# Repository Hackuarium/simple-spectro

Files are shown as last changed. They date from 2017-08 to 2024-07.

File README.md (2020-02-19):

# DIY spectrophotometer

## How to use it ?

Please check the [userguide](docs/5-use) to obtain all the useful information about the user interface.

## Goal of the project

This project was done at the [Hackuarium](http://www.hackuarium.ch/en/) association, a DIY biology hacking-space and open laboratory located in Ecublens (Switzerland). Feel free to [contact us](https://form.jotformeu.com/71600609780354) if you would like additional information or would like to buy a fully built and tested spectrophotometer.

Recently, the open-source and open-hardware community has been involved in the creation of open scientific tools. In this context, a few spectrophotometer projects emerged. However, none of them was sufficiently evolved to be casually used in a laboratory. It is for this reason that we started this project.
Our goal was to create a simple spectrophotometer that measures the
absorbance of a sample for 3 different light colors (red, green, blue), that is
self-contained (battery powered) and displays the result on a LCD screen. In addition, the tool had to be reliable, precise and cheap.

The initial idea was that you could teach spectrophotometry without
having to buy an expensive instrument, since you can find experiments
that do not require a specific light wavelength. This includes
optical density for bacteria culture, determination of a pigment's concentration in
a solution, determination of the kinetic of a reaction and many others.

The device is rather cheap, for you can buy all the components on AliExpress
(but one) and either 3D print or laser cut the case (MDF or acrylic glass). When constructing 10, the price
per spectrophotometer is around $30. However if you want to have a final
product with an aluminium case and PCBs already assembled, the cost would rather be $90 each if you order 20 of them.

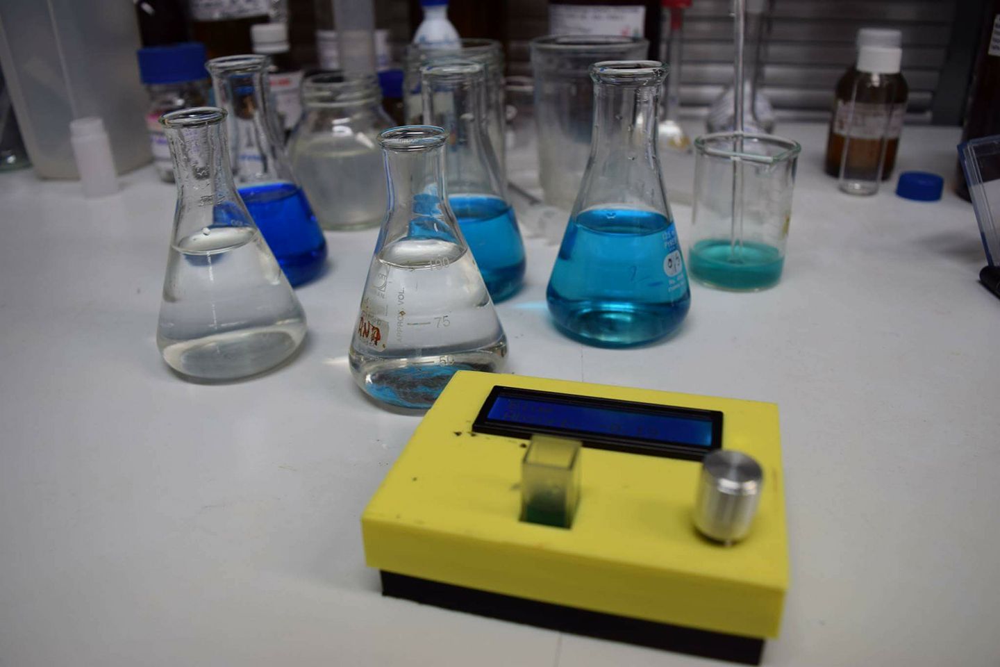
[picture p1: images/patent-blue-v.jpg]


## Can we do science with this ?

Before trying to explain how it is done more in detail maybe the first
question that we should answer is : can we do science with this tool?
When thinking about the design of the spectro, we found an light sensor that converts the light energy to frequency and that is linear on a range of nearly 10^6. This means that the luminosity range that we can measure precisely is really big. Only the precision of the component is therefore really promising and shows that we could do something that gives good results.

And indeed, the final product gives really accurate results in fields like:

- [Chemistry](docs/6-applications/chemistry/README.md)
- [Biology](docs/6-applications/biology/README.md)

And other, which you can see on [our lab notebook](experiments/README.md).

## Some of our results

### Patent blue V

To begin we did a very simple experiment that allows to measure the absorbance of solutions containing different known concentrations of patent blue V (E131), a blue pigment that is used in various blue candies.

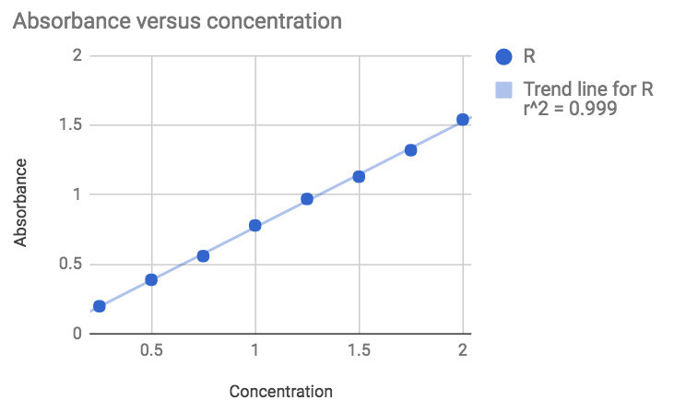
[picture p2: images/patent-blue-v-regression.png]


The result is rather good knowing that the solutions were simply prepared by adding various volumes (0 to 2 mL) of a concentrated pigmented solution with a 1mL seringe to 100mL of water. Not the most accurate method...

### Escherichia coli

Another feature of the simple-spectrophotometer is that it works on a rechargeable battery (autonomy of 48 hours). Consequently, you can measure a kinetic by placing the device directly inside an incubator, which is not feasible with a regular commercial spectrophotometer.

Optical density (OD) at 600nm is often used in biology to determine the biomass increase versus time. In this experiment we have placed Escherichia coli with cell growing media directly in the spectrophotometer cuvette and placed the spectrophotometer itself on a shaker in the incubator.
We can then program it to measure the absorbance every X seconds. In our case we measured the absorbance every 30 minutes (up to 40 measures). The following curve was obtained.

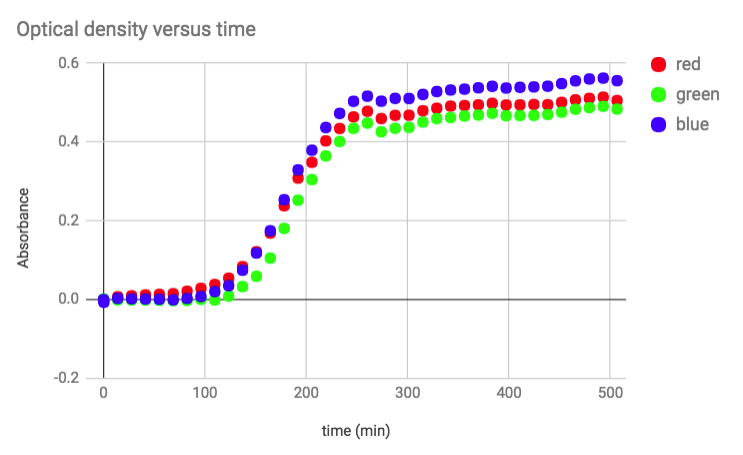
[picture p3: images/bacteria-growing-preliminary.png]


This experiment clearly shows the log phase and the stationary phase. But the growth was faster than expected. An acquisition every 15 minutes would have been a better choice.

## Using the simple spectrophotometer to teach science

The use of the spectrophotometer is rather simple. Just put a blank, press the button, wait 10s and put the sample. The result is displayed on the screen. In addition, it could be open so that students could see how it is inside and could really understand how the tool works (avoiding the "black box" effect). Also, since it is inexpensive, having ten of these for a classroom would be possible, which would allow students to have one instrument per pair.

[Using the spectrophotometer](https://www.youtube.com/watch?v=ZfckWQn0Nws)

For all this reason, we also consider our instrument as a pedagogical tool. This allowed us to use it to teach some basic scientific concepts to groups of children and teenagers.

[School in Mondomo (Colombia)](https://www.youtube.com/watch?v=Be6p4-nW06k)

## How to make it ?

The electronic design is compatible with the Arduino platform. We use an
ATMEGA32U4 microcontroller which is directly connected to the peripherals we need for this spectrophotometer.

We prefer to design the full PCB rather than to make a shield for an existing Arduino board. Indeed, the extra work to add the microcontroller is rather limited, so it does not make sense from our point of view to create a shield. Also, the resulting board is smaller and more reliable.

All the components we use but one are mainstream and can be found on eBay or AliExpress. The only special component is the light to frequency converter [TSL235R](https://www.sparkfun.com/datasheets/Sensors/Imaging/TSL235R-LF.pdf)
that we buy on [Mouser website](http://www.mouser.com).

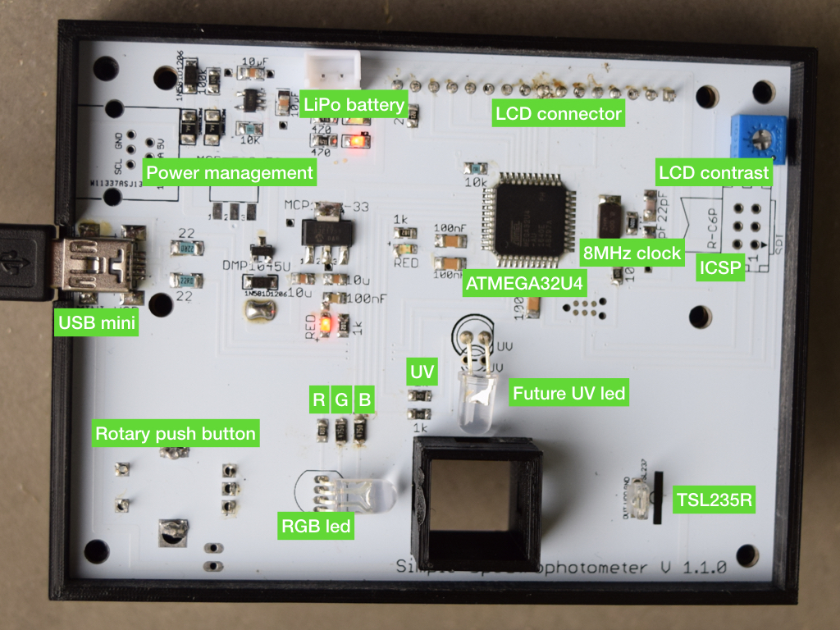
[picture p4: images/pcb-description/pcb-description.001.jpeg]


For more details about the construction process, follow one of the links underneath.

- [The PCB](docs/1-pcb) (using eagle)
- [The case](docs/2-case) (using FreeCAD and OpenSCAD)
- [The software](docs/3-software) (using Arduino)

## Experiments

- [Bacteria growth](experiments/bacteria/README.md)
- [Pigment concentration](experiments/color/README.md)
- [Measure of the fluorescence](experiments/fluorescence/README.md)
- [Kinetic of a reaction](experiments/kinetic/README.md)

## Tests

Underneath, you will find some of the tests we have run to verify the quality of our spectrophotometer.

- [Battery](docs/4-tests/battery)
- [Reproducibility of results](docs/4-tests/stability)

# Workshop

We regularly organize one day workshops "Build your own spectrophotometer" during which the participants learn all the process we went through to obtain the final product and build their own spectrophotometer. Please [contact us](https://form.jotformeu.com/71600609780354) if you are interested by this kind of workshop.

Here are the slides of the presentation we make during the workshop.

- [Slides](docs/7-misc/workshop/slides.pdf)

## Cloning the project

This project uses SUBMODULES.

In order to clone it use:

`git clone --recurse-submodules https://github.com/hackuarium/simple-spectro`

To update the submodules:

`git submodule update --recursive --remote`

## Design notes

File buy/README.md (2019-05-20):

## Buy the spectrophotometer

## DIY versions

The DIY versions are spectrophotometers to assemble yourself. You receive a preprogrammed PCB (all the SMD components are already soldered) as well as all the through holes components and parts to build a case.

### Eco-spectro

You receive all the required parts to construct a spectrophotometer and a case in MDF.

**Price:** 60 CHF + shipping (10 CHF)

### Bio-spectro

You receive all the required parts to construct a spectrophotometer and a case in black plexiglass.

**Price:** 70 CHF + shipping (10 CHF)

### Chimio-spectro

You will receive a case in black plexiglass with a transparent background so that you can easily understand how it works and explain it to others.

You will also get 50mg of E131 that allows to determine the concentration of pigments present in candies.

**Price:** 70 CHF + shipping (10 CHF)

### How to buy it

You can directly buy it online and receive it via mail at your place.

Please note that if you want to power it with a battery you have to buy one yourself.

<form action="https://www.paypal.com/cgi-bin/webscr" method="post" target="_top">
<input type="hidden" name="cmd" value="_s-xclick">
<input type="hidden" name="hosted_button_id" value="76TH95GMW5DSS">
<table>
<tr><td><input type="hidden" name="on0" value="Select the DIY model">Select the DIY model</td></tr><tr><td><select name="os0">
	<option value="Eco spectro">Eco spectro 60.00 CHF</option>
	<option value="Bio spectro">Bio spectro 70.00 CHF</option>
	<option value="Chimio spectro">Chimio spectro 70.00 CHF</option>
</select> </td></tr>
</table>
<input type="hidden" name="currency_code" value="CHF">
<input type="image" src="https://www.paypalobjects.com/en_US/CH/i/btn/btn_buynowCC_LG.gif" border="0" name="submit" alt="PayPal - The safer, easier way to pay online!">

</form>

## Pro version

The pro spectro comes fully assembled, tested and in an aluminium milled anodised case.

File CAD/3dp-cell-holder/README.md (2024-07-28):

# Goal
This 3D printed part allows the replacement of the four small parts holding the test sample cell while letting light pass through small orifices.

# Advantages of this design
- Fewer parts make the assembly easier.
- The cell is better held, preventing variation in results due to changes in the orientation of the cell.
- A side extension wall prevents the UV LED from directly lighting the sensor.
- A bottom wall prevents light from coming through gaps at the bottom of the cell, ensuring more consistency in test conditions.

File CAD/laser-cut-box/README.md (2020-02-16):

## Using lightburn

Preferences may change depending the cutting machine. In our case:

- add an offset of 0.07 on all inside parts (assemble)
- power 100% speed 18%

## It's in the box

#### An OpenSCAD project to wrap your PCB in a box

Often we need to create custom boxes to wrap a printed circuit board (PCB) and this
may be time consuming.

In this project based on couple of parameters you can quickly and efficiently create DXF files that after laser cutting will provide the different elements to create the box. You may cut any number of holes (round or rectangle) on all the faces of the box and the coordinates will always be relative to the (0,0) that is the bottom left of the PCB.

Coordinates [x,y] of holes corresponds to the center.

You can render the box as a 3D image



And you can also export easily as a SVG of DXF file for laser cutting.



## How to use it

Download OpenSCAD and open the file 'testBox.scad'.

The comments in the file should be clear enough to use this code.

## Exporting as DXF

You should change the following parameters before generating DXF:

- showLabels = false
- 3d = false

You may then render the image and export as DXF.

## Code example

```js
$fn=40;

use <pcbbox/pcb.scad>;

pcb(
    length=100,         // length of the PCB
    width=80,           // width of the PCB
    padding=1,          // space around the pcb (between pcb and box)
    thickness=3,        // thickness of the material to create the box
    pcbThickness=1.6,   // thickness of the box
    topToTop=20,        // distance from the top of the PCB to the external top of the box
    bottomToBottom=40,  // distance from the bottom of the PCB to the external bottom of the box
    extend=10,          // should top and bottom 'extend' in order to assemble the box without glue
    screws=[            // position of holes to fix the PCB
        [5,5],
        [10,70],
        [85,15],
        [80,60]
    ],
    screwDiameter=3,    // diameter of the screws to fix the PCB
    topHoles=[          // holes to put on the top of the box
        [20,20,30,10]   // 0,0 is the bottom left of the PCB
    ],
    bottomHoles=[       // holes to put on the bottom of the box
        [40,40,10],     // array witlh 3 parameters = a circle [x,y,diameter]
        [20,20,5,5]     // array with 4 parameters = a rectangle [x,y,width,depth]
    ],
    frontHoles=[        // holes in front of the box, over the PCB
        [20, 2.5, 5],
        [40,5,10,10]
    ],
    frontHolesB=[       // holes in front of the box, under the PCB
        [20,2.5,5],
        [40,5,10,10]
    ],
    backHoles=[         // holes in the back of the box, over the PCB
        [20,2.5,5],
        [40,5,10,10]
    ],
    backHolesB=[        // holes in front of the box, under the PCB
        [20,2.5,5],
        [40,5,10,10]
    ],
    leftHoles=[         // holes on the left of the box, over the PCB
        [20,2.5,5],
        [40,5,10,10]
    ],
    leftHolesB=[        // holes on the left of the box, under the PCB
        [20,2.5,5],
        [40,5,10,10]
    ],
    rightHoles=[        // holes on the right of the box, over the PCB
        [20,2.5,5],
        [40,5,10,10]
    ],
    rightHolesB=[       // holes on the right of the box, under the PCB
        [20,2.5,5],
        [40,5,10,10]
    ],
    showLabels=true,    //should we show the labels
    labelsSize=10,      // size of the labels
    3d=true             // 3d rendering or just 2d ?
);
```

## Screwing the PCB

We recently often use black nylon M3 screw, standoff and spacer.

In order to fix the PCB we have the following sequence:

- M3 screw
- top of the case
- column standoff female spacer
- PCB
- column standoff male spacer
- bottom of the case
- M3 screw (we take 40 mm screws that we cut if needed)



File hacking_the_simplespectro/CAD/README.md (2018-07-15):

This folder contains the files of the final version of the spectro-plongeur. The svg files can be opened in easel.inventables.com (a free account can be created) to change the cut settings and start the CNC (an X-Carve 1000mm x 1000mm).

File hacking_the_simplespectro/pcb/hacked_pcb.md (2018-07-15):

# What has been modified on the PCB ?

- 2 blue LEDs instead of 1 UV and 1 RGB (2 pins are not used)
- 22 Ohm blue LED resistance instead of 1000 Ohm so that both LEDs have equal power
- cables (26W) to connect the PCB to the spectro-plongeur

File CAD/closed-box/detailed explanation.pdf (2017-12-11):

## Spectrophotometer

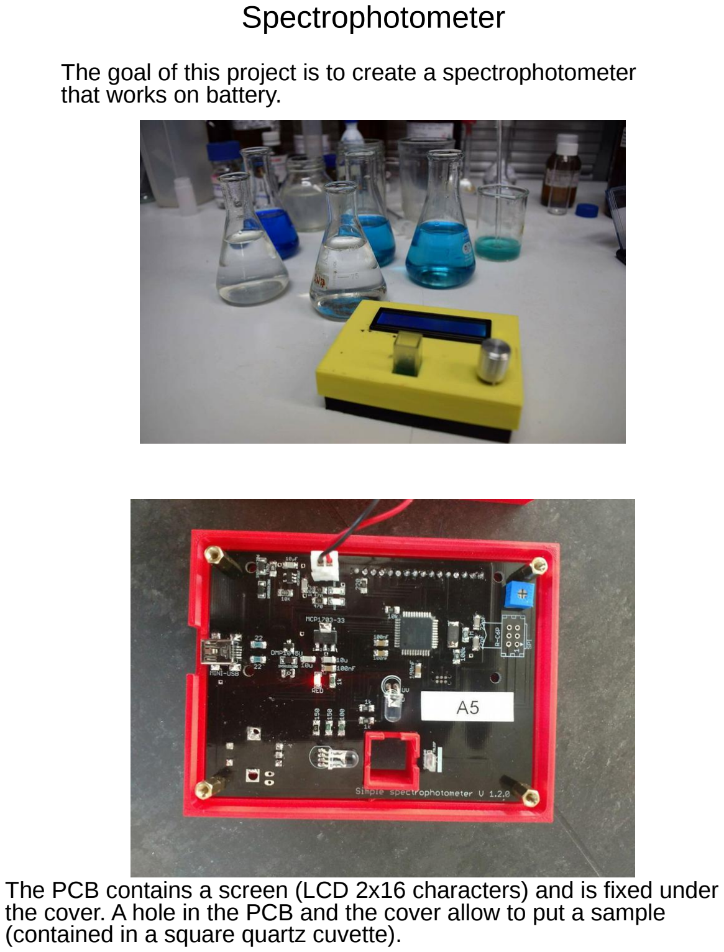
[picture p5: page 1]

The goal of this project is to create a spectrophotometer that works on battery.

The PCB contains a screen (LCD 2x16 characters) and is fixed under the cover. A hole in the PCB and the cover allow to put a sample (contained in a square quartz cuvette).

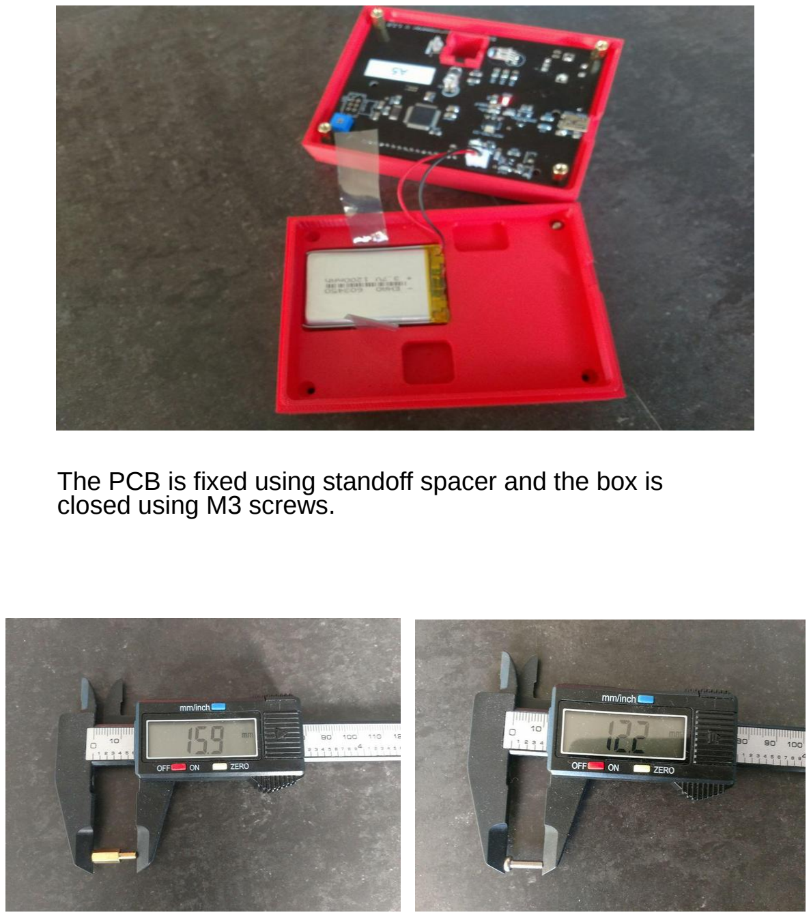
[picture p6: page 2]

The PCB is fixed using standoff spacer and the box is closed using M3 screws.

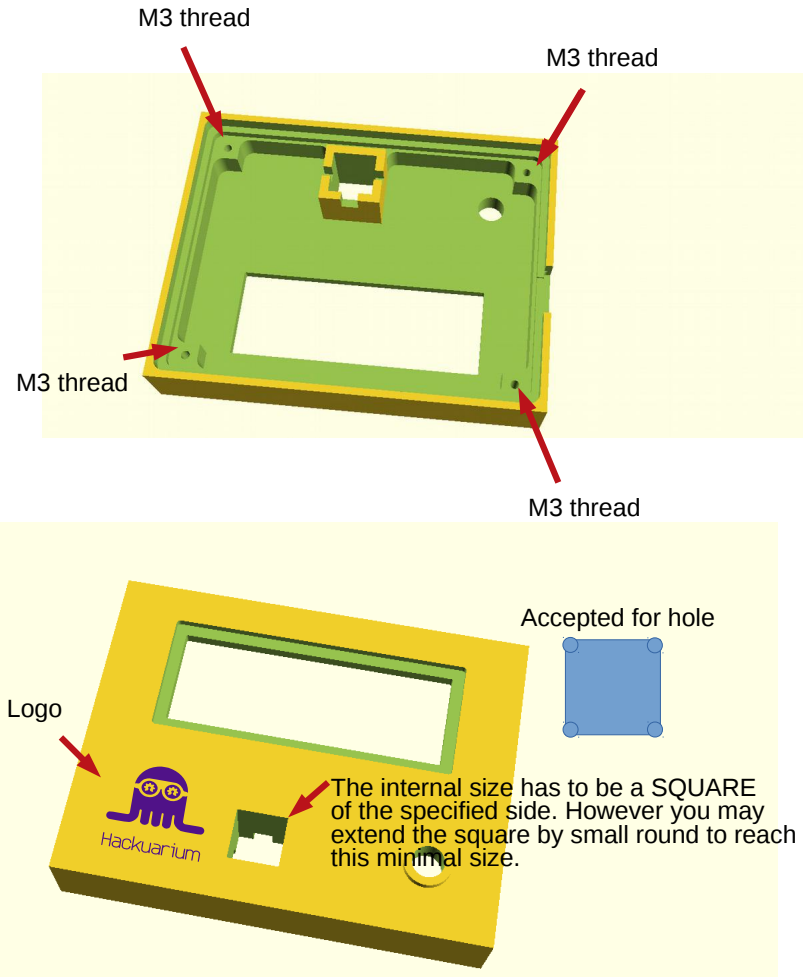
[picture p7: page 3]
M3 thread; Logo

Accepted for hole

The internal size has to be a SQUARE
of the specified side. However you may
extend the square by small round to reach
this minimal size.

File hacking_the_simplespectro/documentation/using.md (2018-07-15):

# How to use the spectro-plongeur ?

The spectro-plongeur can be used in the same way as the simple-spectro; refer to https://github.com/Hackuarium/simple-spectro/tree/master/docs/5-use. The long end allows it to be fastened in the cover of a bioreactor.

## Further development: automatic mode

The objective would be to control the spectro-plongeur from a RaspberryPI to enable automatic measurement of absorbance in the bioreactor https://github.com/Bioreactor/Bioreactor_v4.

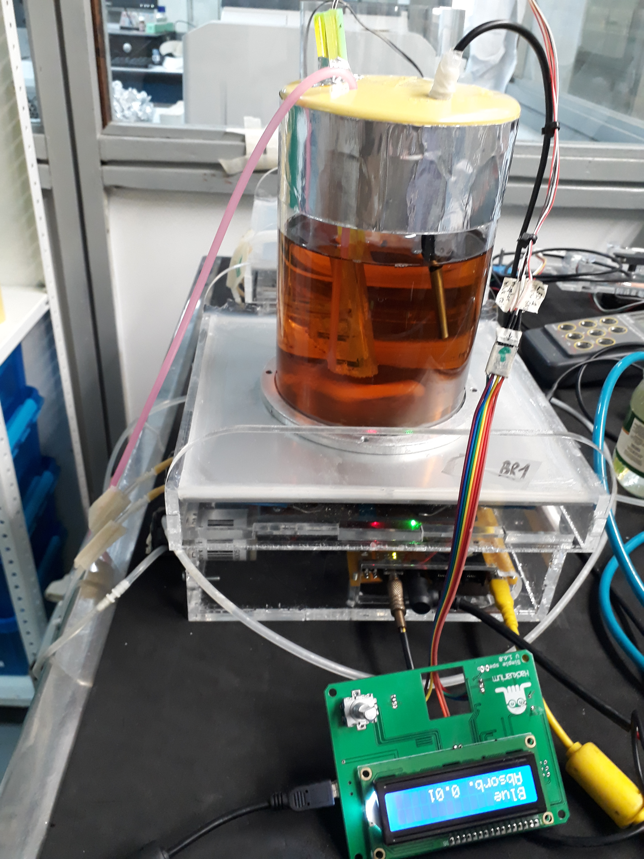
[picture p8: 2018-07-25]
hacking_the_simplespectro/images/bio_temp_spectro.jpg

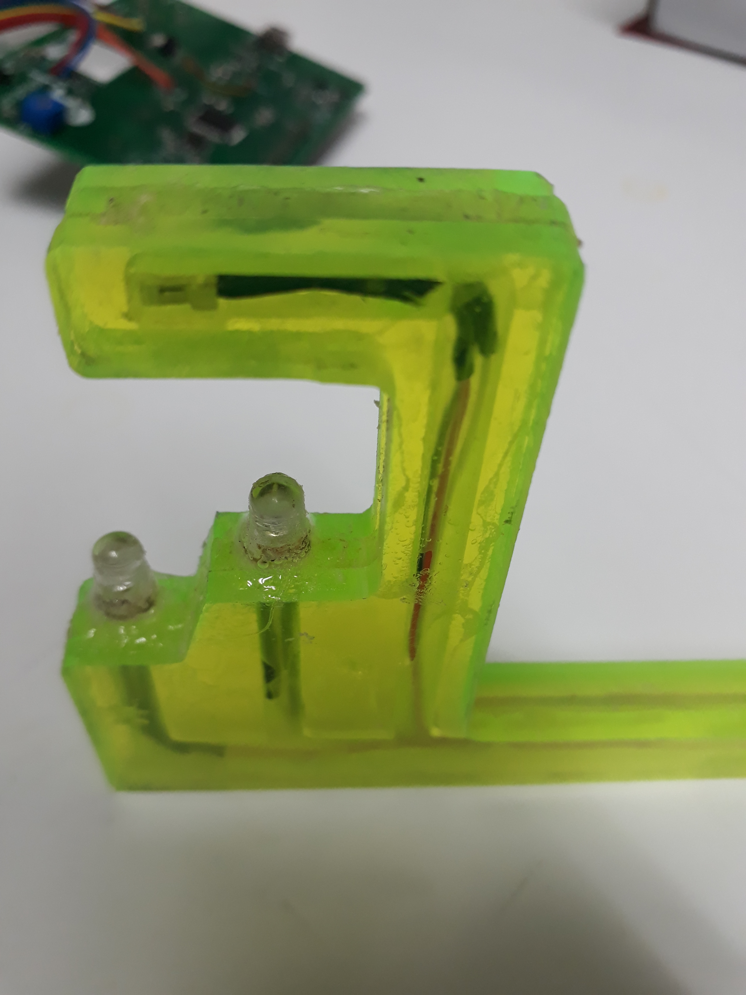
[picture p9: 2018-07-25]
hacking_the_simplespectro/images/spectro_plongeur_2.jpg

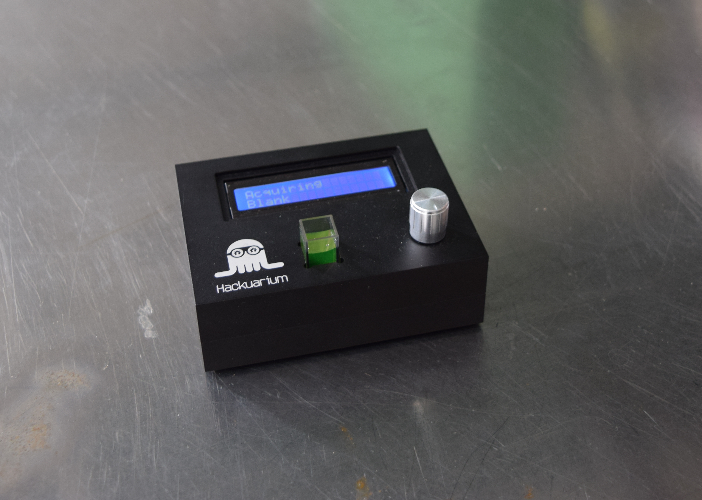
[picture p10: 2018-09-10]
images/spectro.jpg

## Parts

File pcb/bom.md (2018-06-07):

| Kind            |  Value         |  Package        |  Qty  |
| ----------------|----------------|-----------------|-------|
| Battery         |  LiPo 4.2v     |                 |  1    |
| Capacitor       |  100nF         |  1206           |  6    | x
| Capacitor       |  10u           |  1206           |  5    | x
| Capacitor       |  18pF          |  1206           |  2    | x
| Connector       |  BAT           |  2.54mm         |  1    | x
| Crystal         |  8MHz          |  6035           |  1    | x
| ICSP            |  ICSP          |  2 x 3, 2.54mm  |  1    | -
| ICSP            |  TINYISP       |  Tag connect    |  1    | x
| Jumper          |  Jumper        |  2.54mm         |  2    | x
| LCD             |  LCD-HD447804  |  16x1 2.54mm    |  1    | 8
| Led             |  GREEN         |  1206           |  1    | x
| Led             |  RGB-COMMON-CAT|  RGB 5mm led    |  1    |
| Led             |  Blue          |  5mm            |  1    |
| Led             |  Blue / Violet |  3mm            |  1    |
| Light detector  |  TSL237        |  3x1 2.54mm     |  1    |
| LiPo charger    |  MCP73831T     |  SOT23-5        |  1    | x
| Microcontroller |  ATMEGA32U4-AU |  TQFP44         |  1    |
| Mini USB        |  MINI-USB      |  32005-201      |  1    | x  
| Power switch    |  BSP75         |  SOT223         |  1    |
| Regulator       |  MCP1703-33    |  SOT223         |  1    | x
| Resistor        |  0             |  1206           |  1    |
| Resistor        |  22            |  1206           |  3    | x
| Resistor        |  100           |  1206           |  1    | x
| Resistor        |  220           |  1206           |  1    | x
| Resistor        |  100k          |  1206           |  2    | x
| Resistor        |  10k           |  1206           |  5    | x
| Resistor        |  1k            |  1206           |  4    | x
| Resistor        |  1M            |  1206           |  3    | x
| Rotary Encoder  |  EC11E         |  EC11E          |  1    | 9
| Schottky        |  1N5817        |  1206           |  2    | x
| T° sensor       |  NCT175DMR2G   |  Micro8         |  1    |
| Transistor      |  DMP1045U      |  SOT-23         |  1    | x
| Trimmer         |  10k           |  3362P          |  1    | x

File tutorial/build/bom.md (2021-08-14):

# Components to assemble the spectro

## PCB

| Description                | Quantity      | Stock |
| -------------------------- | ------------- | ----- | --- | ------------------------ |
| PCB assembled              | 1             | 17    | 10  | ordered                  |
| TSL 237                    | 1             | 107   | 3   | ok                       |
| JST XH 2p                  | 1             | > 100 | 0.1 | ok                       |
| RGB LED Common cathode 5mm | 1             | 93    | 0.1 | ok                       |
| Blue LED 5mm               | 1             | > 200 | 0.1 | ok                       |
| heat-shrinkable tube 8mm   | 1             | > 1m  | 0.1 | ok                       |
| Trimmer 10k 3362P          | 1             | 14    | 0.1 | 100 ordered (ebay)       |
| LCD 2x16 3.3v (vert)       | 1             | 56    | 2.2 | 50 ordered (aliexpress)  |
| Pin row 2.54mm s           | 1             | 50    | 0.1 | 100 ordered (ebay)       |
| Rotary push                | 1             | 35    | 0.5 | 100 ordered (aliexpress) |
| Conformal coating          | 1 for 50 PCBs | 0     | 0.5 | to order @ distrelec     |

Total price: 16.3 CHF

## Case

| Description               | Quantity | Stock |
| ------------------------- | -------- | ----- | --- | ------------------------ |
| Laser cut box             | 1        | nd    | 3   |
| Screw M3 black nylon 6mm  | 4        | nd    | 0.1 | 300 ordered (aliexpress) |
| Screw M3 black nylon 15mm | 4        | nd    | 0.1 | 300 ordered (aliexpress) |
| Spacer M3 M/F 8mm         | 4        | nd    | 0.1 | 250 ordered (aliexpress) |
| Spacer M3 M/M 12mm        | 4        | nd    | 0.1 | 400 ordered (aliexpress) |
| Rubber feet               | 4        | 192   | 0.1 | to order @ distrelec     |
| Scratch male 30mm         | 1        |       | 0.1 | ok                       |
| Scratch female 30mm       | 1        |       | 0.1 | ok                       |
| Button                    | 1        | 50    | 0.4 | 100 ordered (ebay)       |
| Battery 4.2v              | 1        | 55    | 3.4 | 50 ordered (ebay)        |

Total: 7.4 CHF

## Other

| Description                   | Quantity | Stock |
| ----------------------------- | -------- | ----- | --- | -------------------- |
| USB cable                     | 1        | 105   | 0.5 | ok                   |
| Cuvette                       | 2        | 100   | 0.6 | ok                   |
| Sticker                       | 1        | 100   | 0.1 | ok                   |
| Bag case 120x170              | 1        | 0     | 0.1 | ordered (aliexpress) |
| Bag component 110x160         | 1        | 60    | 0.1 | ok                   |
| Bag experiment + cable 130x90 | 1        | 100   | 0.1 | ok                   |

Total: 1.5 CHF

Total: 25.2 CHF

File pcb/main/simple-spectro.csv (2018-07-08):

Part | Value | Device | Package | Description | ELECROW | LCSC | MF | MPN | OC_FARNELL | OC_NEWARK
C1 | 18pF | C-EUC0805K | C0805K | CAPACITOR, European symbol | C1797 | C1797 |  | 77-VJ1206A180JXXPBC
C10 | 100nF | C-EUC0805K | C0805K | CAPACITOR, European symbol | C49678 | C49678 |  | 80-C1206C104K5R
C11 | 100nF | C-EUC0805K | C0805K | CAPACITOR, European symbol | C49678 | C49678 |  | 80-C1206C104K5R
C12 | 10u | C-EUC0805K | C0805K | CAPACITOR, European symbol | C15850 | C15850 |  | 77-VJ1206V106ZXQTBC
C13 | 100nF | C-EUC0805K | C0805K | CAPACITOR, European symbol | C49678 | C49678 |  | 80-C1206C104K5R
C2 | 18pF | C-EUC0805K | C0805K | CAPACITOR, European symbol | C1797 | C1797 |  | 77-VJ1206A180JXXPBC
C3 | 100nF | C-EUC0805K | C0805K | CAPACITOR, European symbol | C49678 | C49678 |  | 80-C1206C104K5R
C4 | 10u | C-EUC0805K | C0805K | CAPACITOR, European symbol | C15850 | C15850 |  | 77-VJ1206V106ZXQTBC
C5 | 10u | C-EUC0805K | C0805K | CAPACITOR, European symbol | C15850 | C15850 |  | 77-VJ1206V106ZXQTBC
C6 | 10u | C-EUC0805K | C0805K | CAPACITOR, European symbol | C15850 | C15850 |  | 77-VJ1206V106ZXQTBC
C7 | 100nF | C-EUC0805K | C0805K | CAPACITOR, European symbol | C49678 | C49678 |  | 80-C1206C104K5R
C8 | 10u | C-EUC0805K | C0805K | CAPACITOR, European symbol | C15850 | C15850 |  | 77-VJ1206V106ZXQTBC
C9 | 100nF | C-EUC0805K | C0805K | CAPACITOR, European symbol | C49678 | C49678 |  | 80-C1206C104K5R
D1 | Schottky | MBR0520LT | SOD123 | SCHOTTKY BARRIER RECTIFIER |  | C82544 |  | 621-1N5819HW-F
D2 | Schottky | MBR0520LT | SOD123 | SCHOTTKY BARRIER RECTIFIER |  | C82544 |  | 621-1N5819HW-F
D3 | Schottky | MBR0520LT | SOD123 | SCHOTTKY BARRIER RECTIFIER |  | C82544 |  | 621-1N5819HW-F
IC1 | 32U4 | ATMEGA32U4-AU | TQFP44 | http://www.ladyada.net/library/eagle |  | C44854 |  | 556-ATMEGA32U4RC-AU
IC2 | MCP73831T | MCP73831/2 | SOT23-5 | MCP73831/2 LIPO Charger |  | C14879 |  | 579-MCP73831T-3ACIOT
IC3 | MCP1703-33-CB | MCP1703CB | SOT23 | 250 mA, 16V, Low Quiescent Current LDO Regulator |  | C53352
IC4 | DMP1045U | TRANSISTOR_FET_TSM2301CX | SOT-23 | 20V P-Channel Enhancement Mode MOSFET |  | C110499 |  | 621-DMP1045U-7
R1 | 10k | R-EU_R0805 | R0805 | RESISTOR, European symbol | C17414 | C17414
R10 | 0 | R-EU_R0805 | R0805 | RESISTOR, European symbol | C17477 | C17477
R11 | 100k | R-EU_R0805 | R0805 | RESISTOR, European symbol | C17407 | C17407 |  | RC1206FR-07100KL
R12 | 1M | R-EU_R0805 | R0805 | RESISTOR, European symbol | C17514 | C17514
R13 | 10k | R-EU_R0805 | R0805 | RESISTOR, European symbol | C17414 | C17414
R14 | 100 | R-EU_R0805 | R0805 | RESISTOR, European symbol | C17408 | C17408
R15 | 100k | R-EU_R0805 | R0805 | RESISTOR, European symbol | C17407 | C17407 |  | RC1206FR-07100KL
R16 | 10k | R-EU_R0805 | R0805 | RESISTOR, European symbol | C17414 | C17414
R17 | 10k | R-EU_R0805 | R0805 | RESISTOR, European symbol | C17414 | C17414
R18 | 1M | R-EU_R0805 | R0805 | RESISTOR, European symbol | C17514 | C17514
R19 | 1M | R-EU_R0805 | R0805 | RESISTOR, European symbol | C17514 | C17514
R2 | 100 | R-EU_R0805 | R0805 | RESISTOR, European symbol | C17408 | C17408
R20 | 1k | R-EU_R0805 | R0805 | RESISTOR, European symbol | C17513 | C17513
R3 | 10k | R-EU_R0805 | R0805 | RESISTOR, European symbol | C17414 | C17414
R4 | 22 | R-EU_R0805 | R0805 | RESISTOR, European symbol | C17561 | C17561
R5 | 22 | R-EU_R0805 | R0805 | RESISTOR, European symbol | C17561 | C17561
R6 | 22 | R-EU_R0805 | R0805 | RESISTOR, European symbol | C17561 | C17561 |  | 667-ERJ-8GEYJ101V
R7 | 1k | R-EU_R0805 | R0805 | RESISTOR, European symbol | C17513 | C17513
R8 | 1k | R-EU_R0805 | R0805 | RESISTOR, European symbol | C17513 | C17513
R9 | 1k | R-EU_R0805 | R0805 | RESISTOR, European symbol | C17513 | C17513
U1 | NCT75DMR2G | TMP75DGK | MSOP8 |  |  | C94387
X1 | 8MHz | XTALNX6035 | NX6035 | Low cost SMT crystals, no capacitors included |  | C122522 |  | 729-F60800010
X2 | MINI-USB | MINI-USB-SCHIELD-32005-201 | 32005-201 | MINI USB-B Conector |  | C46391 |  | 649-10033526-N3212LF
Z1 | VARISTOR | VARISTORCN0603 | CT/CN0603 | VARISTOR |  | C126845
Z2 | VARISTOR | VARISTORCN0603 | CT/CN0603 | VARISTOR |  | C126845

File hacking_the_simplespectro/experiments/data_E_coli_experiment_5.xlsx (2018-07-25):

 | Experiment 4 |  |  |  |  |  |  |  |  |  |  |  |  |  |  |  |  |  |  |  |  |  |  |  |  |  |  | Uncertainty
numero | Time [hh:mm] | Comment | Measurements |  |  |  |  |  |  |  |  |  |  |  |  |  |  |  |  |  |  |  |  |  |  |  |  | quantity | abs. uncertainty | units | notes
 |  |  | Spectro 1 | Spectro 2 |  |  |  |  |  |  |  |  |  |  |  |  |  |  |  |  |  |  |  |  |  |  |  | mass of colorant |  | mg | Uncertainty of the reading
 |  |  |  | blue 1 |  |  |  |  |  |  |  |  |  |  | blue 2 / UV |  |  |  |  |  |  |  |  |  |  |  |  | volume of water |  | mL | half of the resolution of the graduated cylinder
 |  |  | Abs. reading | I blank | I test 1 | I test 2 | I test 3 | I test 4 | I test 5 | Avg | std | error | Abs. calculated | Abs. reading | I blank | I test 1 | I test 2 | I test 3 | I test 4 | I test 5 | Avg | std | error | Abs. calculated | Abs. reading | Abs. diff. | error | Concentration uncertainty [mg/L]
0 | 9:51:00 | blank - s0 |  | 37048 | 37275 | 37414 | 37274 | 37707 | 37575 | 37382.16667 | 236.0367909 |  |  | 0.01 | 9723 | 3154 | 1593 | 1176 | 5141 | 69456 | 15040.5 | 26839.04263 |  |  |  |  |  | 0
1 | 10:16:00 | inoculation |  | 37571 | 37463 | 36627 | 37380 | 37348 | 37163 | 37258.66667 | 337.6866398 | 0 | 0 | 0 | 126996 | 128088 | 122073 | 54427 | 27004 | -26 | 76427 | 56712.14003 | 0 | 0 | nan | 0 | 0 | 0
2 | 10:23:00 | s1 |  | 37220 | 37207 | 37503 | 37302 | 37384 | 36673 | 37214.83333 | 287.3766982 | 0.005171102107 | 0.0005112308939 |  | 66 | 15 | 231 | 18 | 419 | 42 | 131.8333333 | 162.0560603 | 0.6235843525 | 2.763221579 |  | 2.762710348 | 0.6236057929 | 231.1396469
3 | 10:27:00 | s1 bis |  | 37530 | 37547 | 37484 | 37492 | 37232 | 37166 | 37408.5 | 165.2728048 | 0.004378900968 | -0.001742985039 | 0 | -13 | -46 | -28 | 12 | -45 | 21 | -16.5 | 28.44468316 | 0.8151013291 | #NUM! | inf | #NUM! | 0.8151130912 | 62768.21397
4 | 10:37:00 | add. Meas. |  | 37175 | 37090 | 37095 | 37142 | 36898 | 37076 | 37079.33333 | 96.26144954 | 0.004094436472 | 0.002095392079 | 0 | -22 | -28 | -67 | -35 | 17 | -36 | -28.5 | 27.17903604 | 0.524773903 | #NUM! | -0.3 | #NUM! | 0.5247898757 | 86002.20361
5 | 11:11:00 | s2 |  | 36208 | 36131 | 36174 | 35854 | 35872 | 36069 | 36051.33333 | 153.200087 | 0.00434732302 | 0.01430597781 | 0 | -17 | 22 | 17 | 7 | 3 | 35 | 11.16666667 | 17.87083285 | 0.7661110042 | 3.83532326 | nan | 3.821017282 | 0.7661233386 | 94926.75663
6 | 11:29:00 | add. Meas. |  | 36506 | 36383 | 36532 | 36524 | 36611 | 35969 | 36420.83333 | 233.2392906 | 0.004819588762 | 0.009877430713 | 0.01 | -5 | 150 | -12 | -30 | -31 | -18 | 9 | 69.81117389 | 3.384113603 | 3.929004303 | inf | 3.919126872 | 3.384117035 | 103959.5462
7 | 12:04:00 | add. Meas. |  | 36117 | 36096 | 36145 | 35966 | 35937 | 35829 | 36015 | 124.0532144 | 0.004210819978 | 0.01474389013 | 0 | 13 | 13 | 7 | -97 | -39 | -5 | -18 | 43.35435388 | 1.094548133 | #NUM! | nan | #NUM! | 1.094556232 | 105264.1749
8 | 12:08:00 | s3 |  | 35844 | 35874 | 35865 | 35901 | 36076 | 35959 | 35919.83333 | 86.1798507 | 0.004071722817 | 0.01589299635 | "-0.00" | 12 | 47 | -52 | -23 | -65 | 12 | -11.5 | 42.80537349 | 1.648343444 | #NUM! | nan | #NUM! | 1.648348473 | 114047.4201
9 |  |  |  |  |  |  |  |  |  | #DIV/0! | #DIV/0! | #DIV/0! | #DIV/0! |  |  |  |  |  |  |  | #DIV/0! | #DIV/0! | #DIV/0! | #DIV/0! |  | #DIV/0! | #DIV/0! | #DIV/0!
10 |  |  |  |  |  |  |  |  |  | #DIV/0! | #DIV/0! | #DIV/0! | #DIV/0! |  |  |  |  |  |  |  | #DIV/0! | #DIV/0! | #DIV/0! | #DIV/0! |  | #DIV/0! | #DIV/0! | #DIV/0!

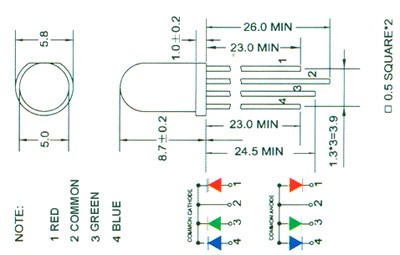
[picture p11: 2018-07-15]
hacking_the_simplespectro/pcb/parts_documentation/doc_RGB_LED.jpg

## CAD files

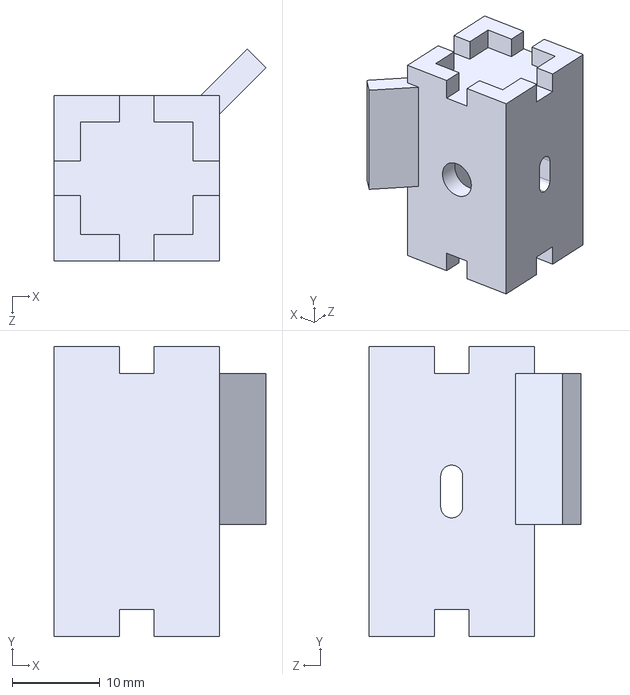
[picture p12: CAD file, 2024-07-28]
CAD/3dp-cell-holder/spectro_cell_holder_3dp.STEP
24.1 x 33.0 x 24.1 mm

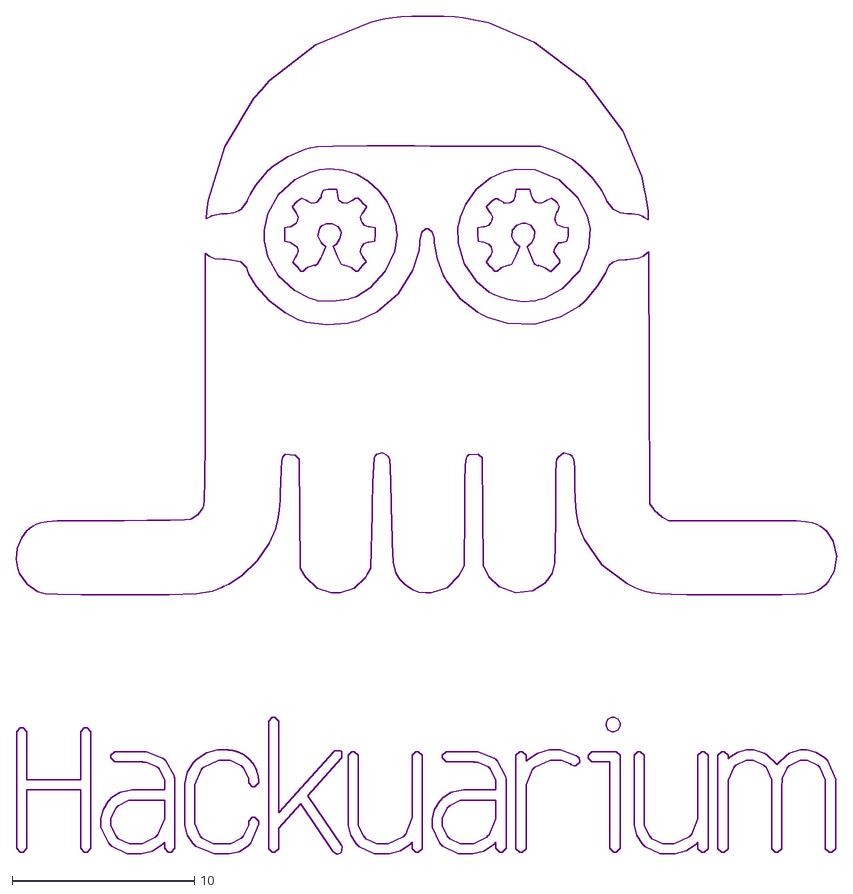
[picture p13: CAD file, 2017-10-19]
CAD/closed-box/logo/logo.dxf
45.0 x 45.9

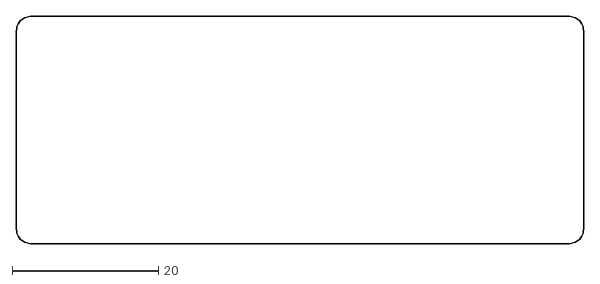
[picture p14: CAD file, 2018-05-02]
CAD/closed-box/screen.dxf
77.6 x 31.1

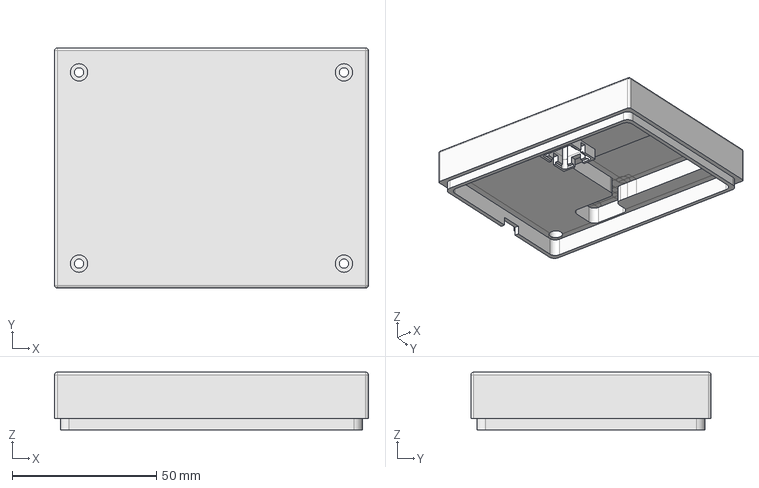
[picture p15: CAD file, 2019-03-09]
CAD/closed-box/step/bottom.step
108.7 x 83.2 x 20.0 mm

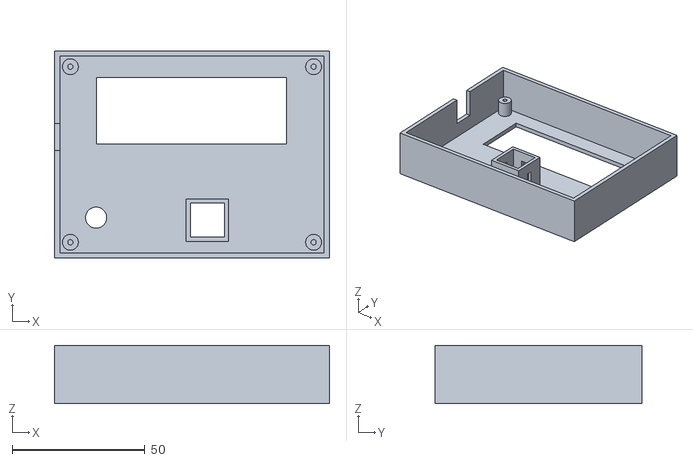
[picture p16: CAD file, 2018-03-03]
CAD/open-box-only-top/top.stl
103.7 x 78.2 x 22.0

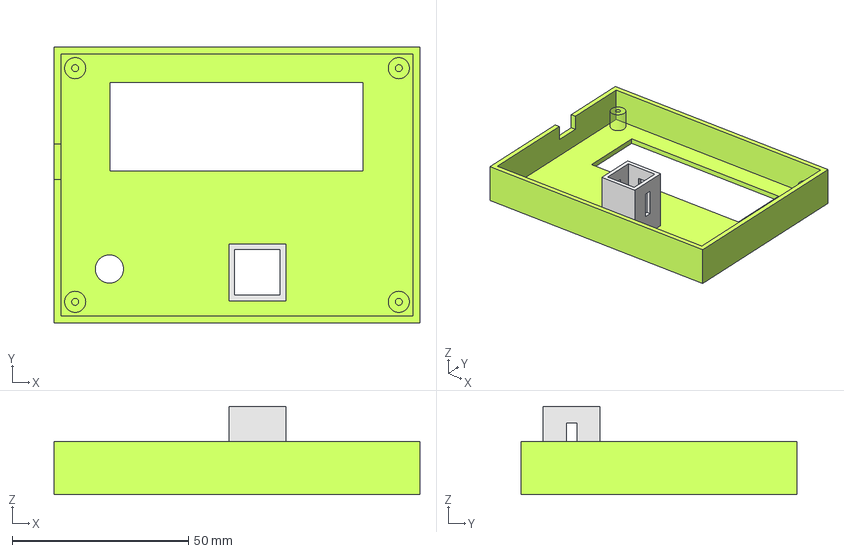
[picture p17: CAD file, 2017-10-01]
CAD/open-box/box.fcstd
103.7 x 78.2 x 25.0 mm
Support001
Support002
Support003
Support004
FinalBox

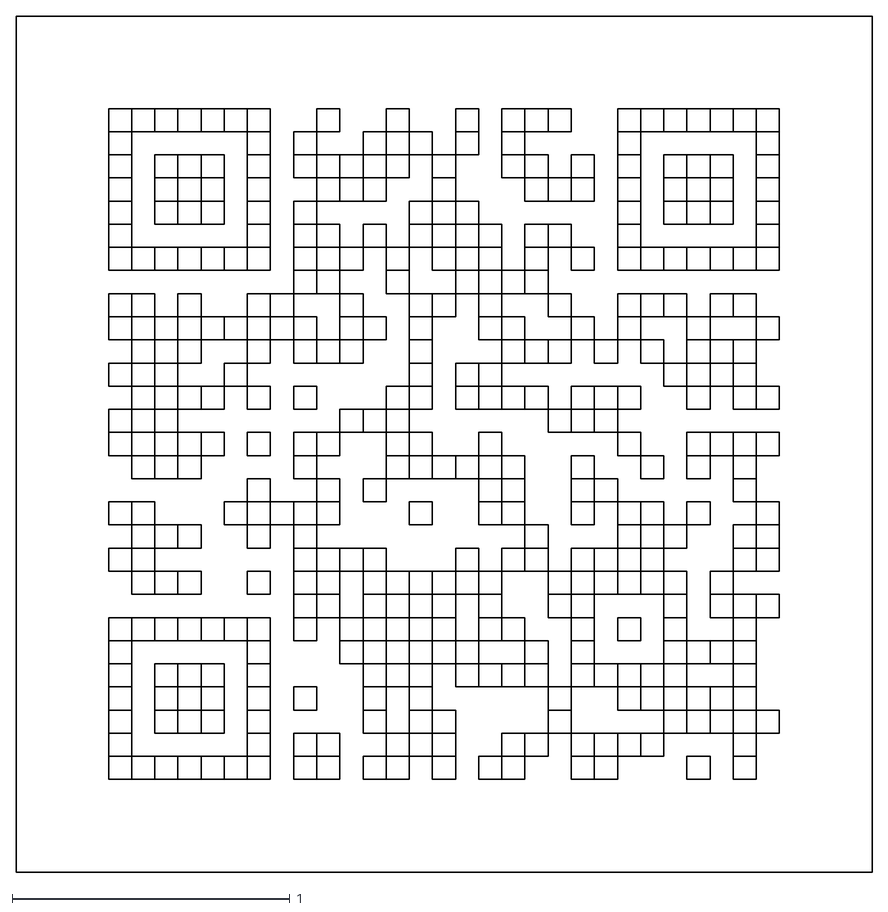
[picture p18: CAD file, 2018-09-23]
CAD/qrcode/github-spectro.dxf
3.08 x 3.08

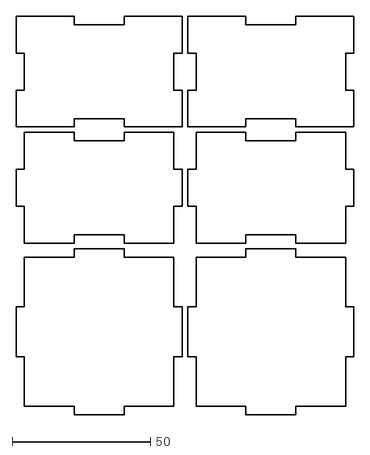
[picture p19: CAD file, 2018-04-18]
tutorial/freecad/60x60x40.dxf
122.0 x 144.0

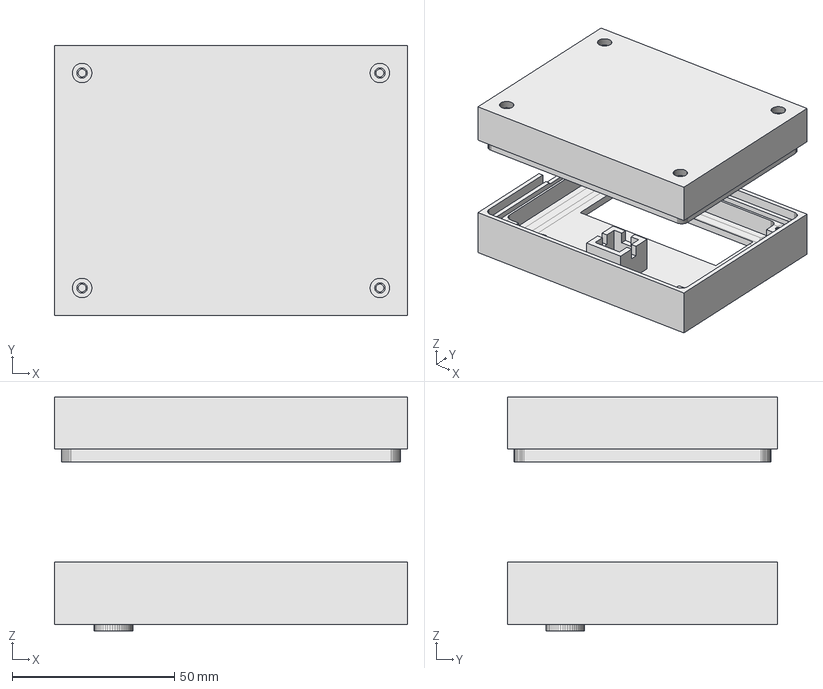
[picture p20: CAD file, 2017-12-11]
CAD/closed-box/model.fcstd
108.7 x 83.2 x 72.0 mm

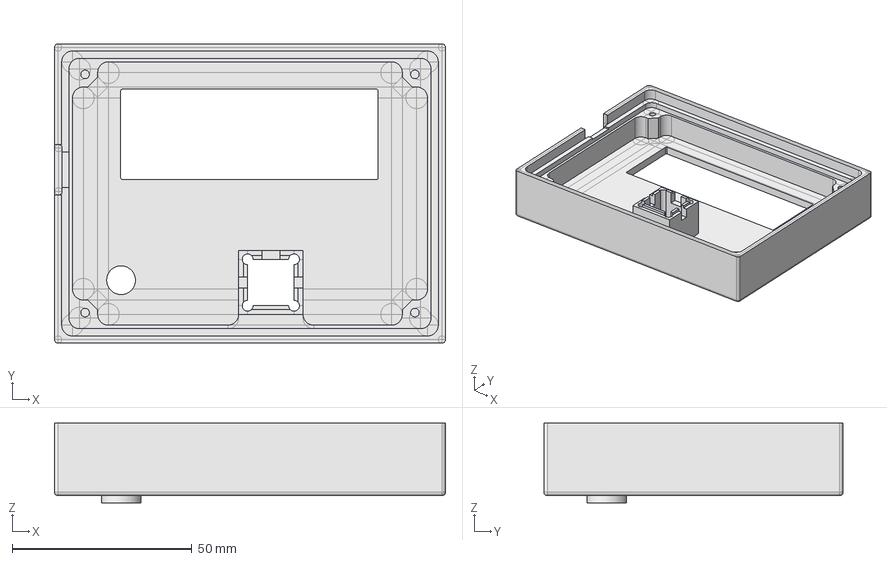
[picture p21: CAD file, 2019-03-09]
CAD/closed-box/step/top.step
108.7 x 83.2 x 22.2 mm

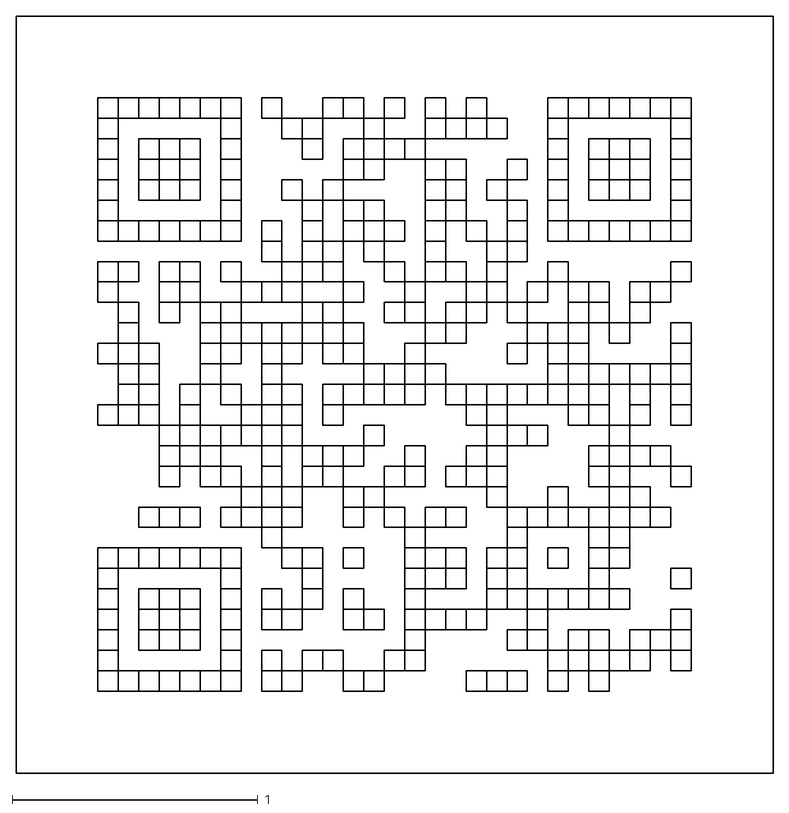
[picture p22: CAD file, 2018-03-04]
CAD/laser-cut-box-freecad/qrcode.dxf
3.08 x 3.08

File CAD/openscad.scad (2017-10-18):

pcbLength=98.7;
pcbWidth=73.2;
pcbThickness=1.6;
pcbSpaceAround=1; // need some space because of rounded angles

sideThickness=4; 
frontThickness=4; 
bottomThickness=6;
bottomHeight=12;
overlap=4; // overlap between top and bottom

shift=pcbSpaceAround+sideThickness;

supportWidth=6;
supportLength=6;
supportHeight=7;
supportHoleX=3.5;
supportHoleY=3.5;
supportHoleR=1.5;
bottomHoleR=3;
bottomHoleHeight=4;

rotaryX=13.2+shift;
rotaryY=12.8+shift;
rotaryR=4;
rotaryExtension=2;
rotaryExtensionR=6;

screenX=13.4+shift;
screenY=40.5+shift;
screenLength=71.6;
screenWidth=25.1;

cuvetteX=48.7+shift;
cuvetteY=5.4+shift;
cuvetteInternal=12.9;
cuvetteThickness=1.6;
cuvetteWindow=3;
cuvetteWindowHeight=5;
cuvetteBottomSpace=2;

batteryX=10+shift;
batteryY=40+shift;
batteryLength=70;
batteryWidth=30;

screenProtectionHeight=1.5;

radius=3; // using bit of 3

usbHeight=5.8;
usbWidth=10;
usbY=38.2+shift;

frontHeight=frontThickness+usbHeight+supportHeight+pcbThickness;

$fn=10;

// PCB
* color("red",0.2)
    translate([shift,shift,-50])
        cube([pcbLength, pcbWidth, pcbThickness]);

// create the bottom part 
*translate([0, 0, 50])
    difference() {
        cube([
            pcbLength+2*pcbSpaceAround+2*sideThickness,
            pcbWidth+2*pcbSpaceAround+2*sideThickness,
            bottomHeight
        ]);
        
        // remove the external border so it fits in the other part
        difference() {
            cube([
                pcbLength+2*pcbSpaceAround+2*sideThickness,
                pcbWidth+2*pcbSpaceAround+2*sideThickness,
                overlap
            ]);
            translate([sideThickness/2, sideThickness/2, 0])
                roundedParallelepiped4(
                    x=pcbLength+2*pcbSpaceAround+sideThickness,
                    y=pcbWidth+2*pcbSpaceAround+sideThickness,
                    z=overlap,
                    r=radius
                );
        }
        
        // remove the hole for cuvette
        translate([
            cuvetteX-cuvetteBottomSpace,
            cuvetteY-cuvetteBottomSpace,
            0
        ])
        roundedParallelepiped4(x=cuvetteInternal+2*cuvetteBottomSpace, y=cuvetteInternal+2*cuvetteBottomSpace, z=bottomHeight-bottomThickness, r=radius);
        
          // remove the hole for battery
        translate([
            batteryX,
            batteryY,
            0
        ])
            roundedParallelepiped4(x=batteryLength, y=batteryWidth, z=bottomHeight-bottomThickness, r=radius);
        
        // make holes for screws        
        translate([shift+supportHoleX, shift+supportHoleY, 0])
            screwHole(rSmall=supportHoleR, rLarge=bottomHoleR, height=bottomHeight, heightLarge=bottomHoleHeight);
        
        translate([shift+pcbLength-supportHoleX, shift+supportHoleY, 0])
            screwHole(rSmall=supportHoleR, rLarge=bottomHoleR, height=bottomHeight, heightLarge=bottomHoleHeight);
        
        translate([shift+supportHoleX, shift+pcbWidth-supportHoleY, 0])
            screwHole(rSmall=supportHoleR, rLarge=bottomHoleR, height=bottomHeight, heightLarge=bottomHoleHeight);
        
        translate([shift+pcbLength-supportHoleX, shift+pcbWidth-supportHoleY, 0])
            screwHole(rSmall=supportHoleR, rLarge=bottomHoleR, height=bottomHeight, heightLarge=bottomHoleHeight);
        
            
    }
    

// create a hole that is smaller in the middle
module screwHole(rSmall=2, rLarge=4, height=10, heightLarge=3) {
    heightSmall=height-2*heightLarge;
    cylinder(r=rLarge, h=heightLarge);
    translate([0,0,heightLarge])
        cylinder(r=rSmall, h=heightSmall);
     translate([0,0,heightLarge+heightSmall])
        cylinder(r=rLarge, h=heightLarge);
}


// create the cuvette
translate([cuvetteX, cuvetteY, 0])
    cuvette(
        frontHeight,
        r=radius,
        cuvetteInternal,
        cuvetteY,
        overlap,
        pcbSpaceAround,
        supportHeight,
        frontThickness,
        pcbThickness,
        screenProtectionHeight
    );

// create the box with the holes
translate([0, 0, 0])
    difference() {
        // the front box
        cube([
            pcbLength+2*pcbSpaceAround+2*sideThickness,
            pcbWidth+2*pcbSpaceAround+2*sideThickness,
            frontHeight
        ]);

        // remove the top layer where the PCB is fixed
        translate([sideThickness, sideThickness, supportHeight + frontThickness])
            roundedParallelepiped4(
                x=pcbLength+2*pcbSpaceAround,
                y=pcbWidth+2*pcbSpaceAround,
                z=frontHeight,
                r=radius
            );
        
        // remove the bottom layer as 2 roundParallelepiped
        translate([sideThickness+supportLength+pcbSpaceAround, sideThickness+pcbSpaceAround, frontThickness])
            roundedParallelepiped4(
                x=pcbLength-2*supportLength,
                y=pcbWidth,
                z=frontHeight,
                r=radius
            );
        translate([sideThickness+pcbSpaceAround, sideThickness+supportWidth+pcbSpaceAround, frontThickness])
            roundedParallelepiped4(
                x=pcbLength,
                y=pcbWidth-2*supportWidth,
                z=frontHeight,
                r=radius
            );
        
        // we need to remove some material so that is fits together
            translate([sideThickness/2, sideThickness/2, frontHeight - overlap])
        roundedParallelepiped4(
            x=pcbLength+2*pcbSpaceAround+sideThickness,
            y=pcbWidth+2*pcbSpaceAround+sideThickness,
            z=frontHeight,
            r=radius
        );
        
        // remove the holes to fix the PCB
        translate([sideThickness+pcbSpaceAround+supportHoleX, sideThickness+pcbSpaceAround+supportHoleY, frontThickness])
            cylinder(r=supportHoleR, h=frontHeight);
        
        translate([sideThickness+pcbSpaceAround+pcbLength-supportHoleX, sideThickness+pcbSpaceAround+supportHoleY, frontThickness])
            cylinder(r=supportHoleR, h=frontHeight);
        
        translate([sideThickness+pcbSpaceAround+supportHoleX, sideThickness+pcbSpaceAround++pcbWidth-supportHoleY, frontThickness])
            cylinder(r=supportHoleR, h=frontHeight);
        
        translate([sideThickness+pcbSpaceAround+pcbLength-supportHoleX, sideThickness+pcbSpaceAround+pcbWidth-supportHoleY, frontThickness])
            cylinder(r=supportHoleR, h=frontHeight);
        
        // remove for the rotary push button
        translate([rotaryX, rotaryY, 0])
            cylinder(r=rotaryR, h=frontThickness);
            
            
        // we will remove the hole for the screen
        translate([screenX, screenY, 0])
            cube([screenLength, screenWidth, frontThickness]);
            
                // create the hole for cuvette
        translate([cuvetteX, cuvetteY, 0])
            cube([cuvetteInternal, cuvetteInternal, frontHeight]);
            
        // remove part for the screen protection
        translate([sideThickness, sideThickness, 0])
            roundedParallelepiped4(
                x=pcbLength+2*pcbSpaceAround,
                y=pcbWidth+2*pcbSpaceAround,
                z=screenProtectionHeight,
                r=radius
            );
        
        // we remove the USB port
        translate([0,usbY,pcbThickness+frontThickness+supportHeight])
            cube([sideThickness,usbWidth,usbHeight]);
    

    }
    
    
    // we add a border around push button
    difference() {
        height=rotaryExtension+screenProtectionHeight;
        translate([rotaryX, rotaryY, -2])
            cylinder(r=rotaryExtensionR, h=height);
        translate([rotaryX, rotaryY, -2])
            cylinder(r=rotaryR, h=height);
    }
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

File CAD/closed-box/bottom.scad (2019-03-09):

use <screwHole.scad>;
use <roundedParallelepiped4.scad>;
use <roundedParallelepiped5.scad>;
use <cubeWithCylinders.scad>;

module bottom() {
        
    
    // create the bottom part 
    translate([0, 0, frontHeight-overlap+1])
        union() {
            difference() {
                
                // the bottom
                translate([0,0,bottomHeight]) mirror([0,0,1]) roundedParallelepiped5(
                    pcbLength+2*pcbSpaceAround+2*sideThickness,
                    pcbWidth+2*pcbSpaceAround+2*sideThickness,
                    bottomHeight,
                    chamfer
                );
         
                // remove the external border so it fits in the other part
                difference() {
                    cube([
                        pcbLength+2*pcbSpaceAround+2*sideThickness,
                        pcbWidth+2*pcbSpaceAround+2*sideThickness,
                        overlap
                    ]);
                    translate([sideThickness/2+bottomClosureSpace, sideThickness/2+bottomClosureSpace, 0])
                        roundedParallelepiped4(
                            x=pcbLength+2*pcbSpaceAround+sideThickness-2*bottomClosureSpace,
                            y=pcbWidth+2*pcbSpaceAround+sideThickness-2*bottomClosureSpace,
                            z=overlap,
                            r=radius
                        );
                }
                
                // remove some volume to have room for pcb
                translate([sideThickness, sideThickness, 0])
                    roundedParallelepiped4(
                        x=pcbLength+2*pcbSpaceAround,
                        y=pcbWidth+2*pcbSpaceAround,
                        z=bottomDigged,
                        r=radius
                    );
                
                // remove the hole for cuvette
                translate([
                    cuvetteX-cuvetteBottomSpace,
                    cuvetteY-cuvetteBottomSpace,
                    0
                ])
                cubeWithCylinders(x=cuvetteInternal+2*cuvetteBottomSpace, y=cuvetteInternal+2*cuvetteBottomSpace, z=bottomHeight-bottomMinimal,  r=radiusCorner);
                
                  // remove the hole for battery
                translate([
                    batteryX,
                    batteryY,
                    bottomDigged
                ])
                    roundedParallelepiped4(x=batteryLength, y=batteryWidth, z=batteryHeight, r=radius);
                 
                 // the hole for the battery connector
                translate([
                    connectorX,
                    connectorY,
                    bottomDigged
                ])
                    roundedParallelepiped4(x=connectorLength, y=connectorWidth, z=connectorHeight, r=radius);
                    
                // small line for battery cable
                translate([
                    connectorX + connectorLength - radius,
                    connectorY,
                    bottomDigged
                ])
                    cube([batteryX-connectorX-connectorWidth + 2 * radius, batteryY + batteryWidth - connectorY, batteryHeight]);
                
                // we remove cutting edges
                translate([
                    batteryX-radius,
                    connectorY-radius,
                    bottomDigged
                ])
                    difference() {
                        cube([radius, radius, batteryHeight]);
                        cylinder(h=batteryHeight, r=radius);
                    };
                
                translate([
                    connectorX + connectorLength + radius,
                    batteryY + batteryWidth+radius-0.001,
                    bottomDigged
                ])
                    difference() {
                        translate([-radius, -radius, 0]) 
                            cube([radius, radius, batteryHeight]);
                        cylinder(h=batteryHeight, r=radius);
                    };
             
                
                
                // we remove the USB port
                translate([0,usbY,0])
                    cube([sideThickness,usbWidth,overlap]);
                // remove some more space so the USB plug fits in
                translate([-usbSpaceThickness,usbY-usbSpace,0])
                    roundedParallelepiped4(
                        x=usbSpaceThickness*2,
                        y=usbWidth+2*usbSpace,
                        z=overlap+usbSpace,
                        r=1
                    );
                
                // make holes for screws        
                echo(bottomSmallHoleR, bottomSmallHoleR);
                translate([shift+supportHoleX, shift+supportHoleY, 0])
                    screwHole(rSmall=bottomSmallHoleR, rLarge=bottomHoleR, height=bottomHeight, heightExternal=bottomHoleExternalHeight, heightInternal=bottomHoleInternalHeight);
                
                translate([shift+pcbLength-supportHoleX, shift+supportHoleY, 0])
                    screwHole(rSmall=bottomSmallHoleR, rLarge=bottomHoleR, height=bottomHeight, heightExternal=bottomHoleExternalHeight, heightInternal=bottomHoleInternalHeight);
                
                translate([shift+supportHoleX, shift+pcbWidth-supportHoleY, 0])
                    screwHole(rSmall=bottomSmallHoleR, rLarge=bottomHoleR, height=bottomHeight, heightExternal=bottomHoleExternalHeight, heightInternal=bottomHoleInternalHeight);
                
                translate([shift+pcbLength-supportHoleX, shift+pcbWidth-supportHoleY, 0])
                    screwHole(rSmall=bottomSmallHoleR, rLarge=bottomHoleR, height=bottomHeight, heightExternal=bottomHoleExternalHeight, heightInternal=bottomHoleInternalHeight);     
            };
            

            /* little border around the cell */ 
            translate([
                cuvetteX-cuvetteBottomSpace-cuvetteThickness,
                cuvetteY-cuvetteBottomSpace-cuvetteThickness,
                overlap-cuvetteTopBottomOverlap
            ])
                color("red")
                difference() {
                    cube([
                        cuvetteInternal+2*cuvetteBottomSpace+2*cuvetteThickness,
                        cuvetteInternal+2*cuvetteBottomSpace+2*cuvetteThickness,
                        bottomHeight-bottomMinimal-overlap
                    ]);

                    // cutting the windows in cuvette ...
                    heightWindow=bottomDigged-overlap;
                    translate([0, cuvetteThickness+(cuvetteInternal-cuvetteWindow)/2, 0])
                        cube([cuvetteThickness, cuvetteWindow, heightWindow]);
                    translate([cuvetteThickness+cuvetteInternal, cuvetteThickness+(cuvetteInternal-cuvetteWindow)/2, 0])
                        cube([cuvetteThickness, cuvetteWindow, heightWindow]);
                    translate([cuvetteThickness+(cuvetteInternal-cuvetteUVWindow)/2, cuvetteThickness+cuvetteInternal, 0])
                        cube([cuvetteUVWindow, cuvetteThickness, heightWindow]);

                    // remove the hole for cuvette
                    translate([
                        cuvetteThickness,
                        cuvetteThickness,
                        0
                    ])
                    cubeWithCylinders(x=cuvetteInternal+2*cuvetteBottomSpace, y=cuvetteInternal+2*cuvetteBottomSpace, z=bottomHeight-bottomMinimal-overlap, r=radiusCorner);
                
                    // cutting the overlap of the well
                    cuvetteInternalOverlapCut = cuvetteThickness/2+0.15;
                    
                    union() {
                        translate([
                            cuvetteThickness,
                            cuvetteThickness-cuvetteInternalOverlapCut,
                            0
                        ])
                            cube([
                                cuvetteInternal+2*cuvetteBottomSpace,
                                cuvetteInternal+2*cuvetteBottomSpace+2*cuvetteInternalOverlapCut,
                                cuvetteTopBottomOverlap
                            ]);
                        translate([
                            cuvetteThickness-cuvetteInternalOverlapCut,
                            cuvetteThickness,
                            0
                        ])
                            cube([
                                cuvetteInternal+2*cuvetteBottomSpace+2*cuvetteInternalOverlapCut,
                                cuvetteInternal+2*cuvetteBottomSpace,
                                cuvetteTopBottomOverlap
                            ]);
                    }
                
                }
            
            
    };
}

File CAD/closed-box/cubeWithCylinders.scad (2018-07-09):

module cubeWithCylinders(x, y, z, r) {
    union() {
        cube([x, y, z]);
        translate([0,0,0]) cylinder(h=z, r=r);
        translate([x,0,0]) cylinder(h=z, r=r);
        translate([0,y,0]) cylinder(h=z, r=r);
        translate([x,y,0]) cylinder(h=z, r=r);
    }
}

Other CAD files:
CAD/closed-box/stl/alu-bottom.stl
CAD/holder.fcstd
CAD/laser-cut-box-freecad/2d-box-spectro.fcstd
CAD/laser-cut-box/4xspectro_center_3_15.dxf
hacking_the_simplespectro/CAD/FCStd/SPECTRO_PLONGEUR_7.FCStd
CAD/closed-box/stl/alu-top.stl
CAD/laser-cut-box/5xspectro_center_3_15.dxf
CAD/closed-box/cuvette.scad
CAD/3dp-cell-holder/spectro_cell_holder_3dp.3mf
CAD/3dp-cell-holder/spectro_cell_holder_3dp.SLDPRT
CAD/closed-box/openscad.scad
CAD/closed-box/pcb.scad
CAD/closed-box/roundedParallelepiped4.scad
CAD/closed-box/roundedParallelepiped5.scad
CAD/closed-box/screen.scad
CAD/closed-box/screwHole.scad
CAD/closed-box/stl/plastic-bottom.stl
CAD/closed-box/stl/plastic-top.stl
CAD/closed-box/top.scad
CAD/laser-cut-box-freecad/2d-box-spectro.dxf
CAD/laser-cut-box/spectro.dxf
CAD/open-box-only-top/box.fcstd
CAD/open-box/bottom.stl
CAD/open-box/top.stl
tutorial/freecad/100x50x30.dxf
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

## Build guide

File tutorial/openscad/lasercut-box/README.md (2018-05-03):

# Laser cut Box OpenSCAD Module

This is an OpenSCAD module for creating boxes to be laser-cut out of
flat panels (e.g. plywood or acrylic). The boxes dimensions are
customizable, supports opening the top, insetting the bottom, and
adding handles.

## Synopsis

```
box(options);
```

## Options

 * width (length) - outer width of box
 * height (length) - outer height of box
 * depth (length) - outer depth of box
 * inner (boolean) - width/height/depth are inner dimensions
 * thickness (length) - material thickness
 * finger_width (length) - target finger width
 * finger_margin (length) - distance from inside edge to first finger
 * open (boolean) - Removes the top
 * inset (length) - Amount to inset the bottom side
 * assemble (boolean) - Render assembled 3D box instead of 2D cutting plans
 * hole_width - Width of handle hole
 * hole_height - Height of handle hole
 * hole_margin - Distance from top edge to handle hole
 * kerf (diameter) - Cutting kerf (rendering will be offset by half this)
 * dividers (array with two elements) - How many dividers to insert in X and Y directions
 * holes (array) - Where to place rivet holes
 * hole_dia (length) - Diameter of rivet holes
 * ears (boolean) - If true, 'ears' for hinges are generated

## Examples

```scad
include <box.scad>
box(width = 120, height = 100, depth = 140, thickness = 4, assemble = true);
```

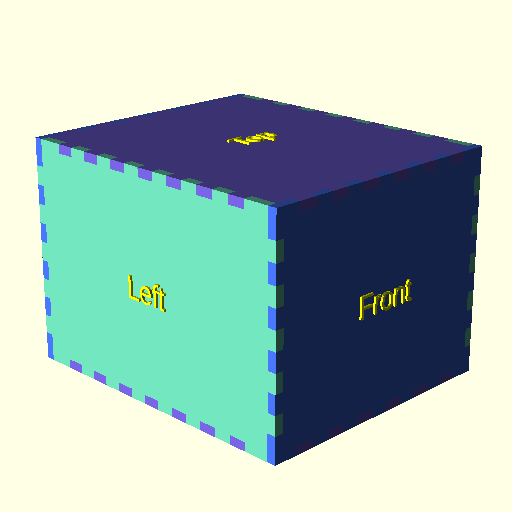
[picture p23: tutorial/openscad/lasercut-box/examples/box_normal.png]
Normal closed box


Dimensions are outer by default. Set ```inner = true``` to render a box based on inner dimensions:

```scad
include <box.scad>
box(width = 120, height = 100, depth = 140, thickness = 4, inner = true, assemble = true);
```

Set ```assemble = false``` to render the final rendering for cutting:

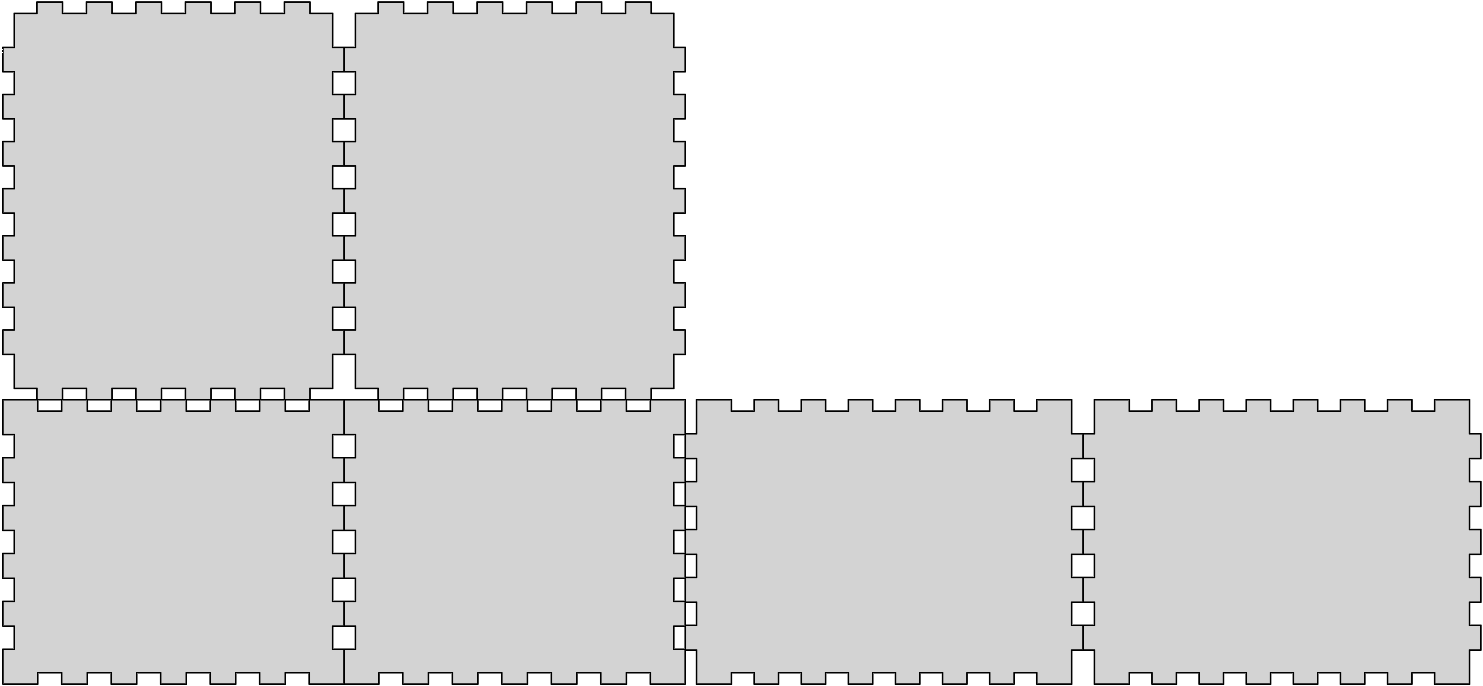
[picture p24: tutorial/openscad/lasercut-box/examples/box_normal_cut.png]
Rendering


Another example with open top and handles:

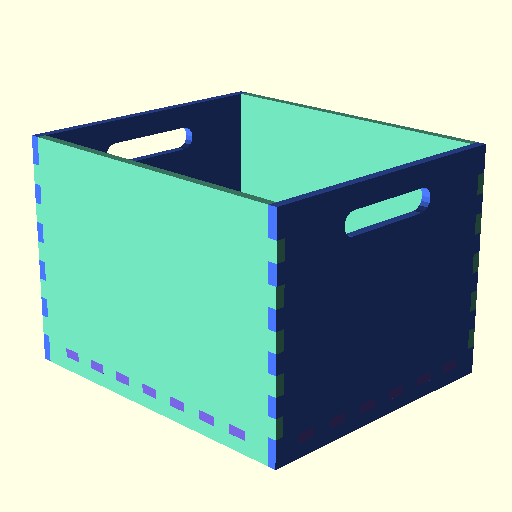
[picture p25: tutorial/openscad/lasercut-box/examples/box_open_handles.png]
Open box with handles


You can use another box as a lid:

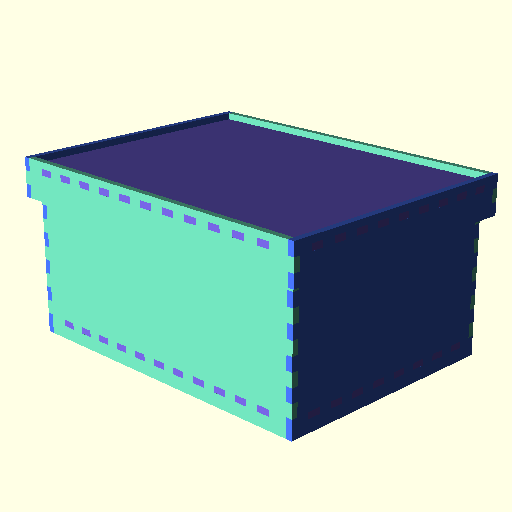
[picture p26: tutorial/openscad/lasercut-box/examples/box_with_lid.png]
Box With lid


The target finger size can be adjusted using the ```finger_width``` option, but it will be adjusted depending on the box dimensions:

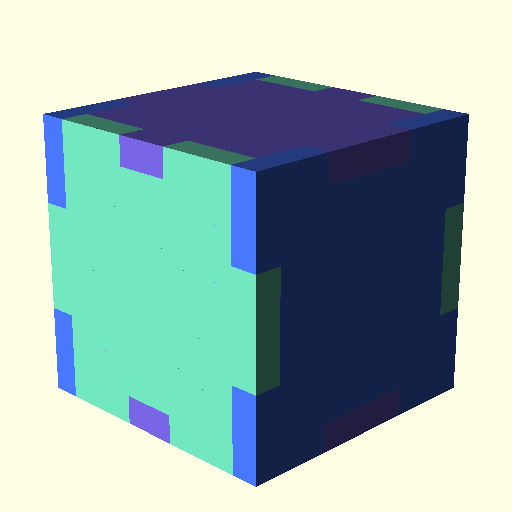
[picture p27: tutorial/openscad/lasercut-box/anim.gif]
Dynamic finger adjustment


## License

Copyright (c) 2016 Lars Christensen

Permission is hereby granted, free of charge, to any person obtaining
a copy of this software and associated documentation files (the
"Software"), to deal in the Software without restriction, including
without limitation the rights to use, copy, modify, merge, publish,
distribute, sublicense, and/or sell copies of the Software, and to
permit persons to whom the Software is furnished to do so, subject to
the following conditions:

The above copyright notice and this permission notice shall be
included in all copies or substantial portions of the Software.

THE SOFTWARE IS PROVIDED "AS IS", WITHOUT WARRANTY OF ANY KIND,
EXPRESS OR IMPLIED, INCLUDING BUT NOT LIMITED TO THE WARRANTIES OF
MERCHANTABILITY, FITNESS FOR A PARTICULAR PURPOSE AND
NONINFRINGEMENT. IN NO EVENT SHALL THE AUTHORS OR COPYRIGHT HOLDERS BE
LIABLE FOR ANY CLAIM, DAMAGES OR OTHER LIABILITY, WHETHER IN AN ACTION
OF CONTRACT, TORT OR OTHERWISE, ARISING FROM, OUT OF OR IN CONNECTION
WITH THE SOFTWARE OR THE USE OR OTHER DEALINGS IN THE SOFTWARE.

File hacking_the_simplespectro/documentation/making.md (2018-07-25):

# How to make the spectro-plongeur ?

## List of materials

- translucent acrylic, 3mm thickness
- sheathing
- self-curing acrylic - autopolimerizable acrylic resin
- silicone glue
- cables 26W 
- a soldered PCB with cables for the two LEDs and the receptor

<figure>
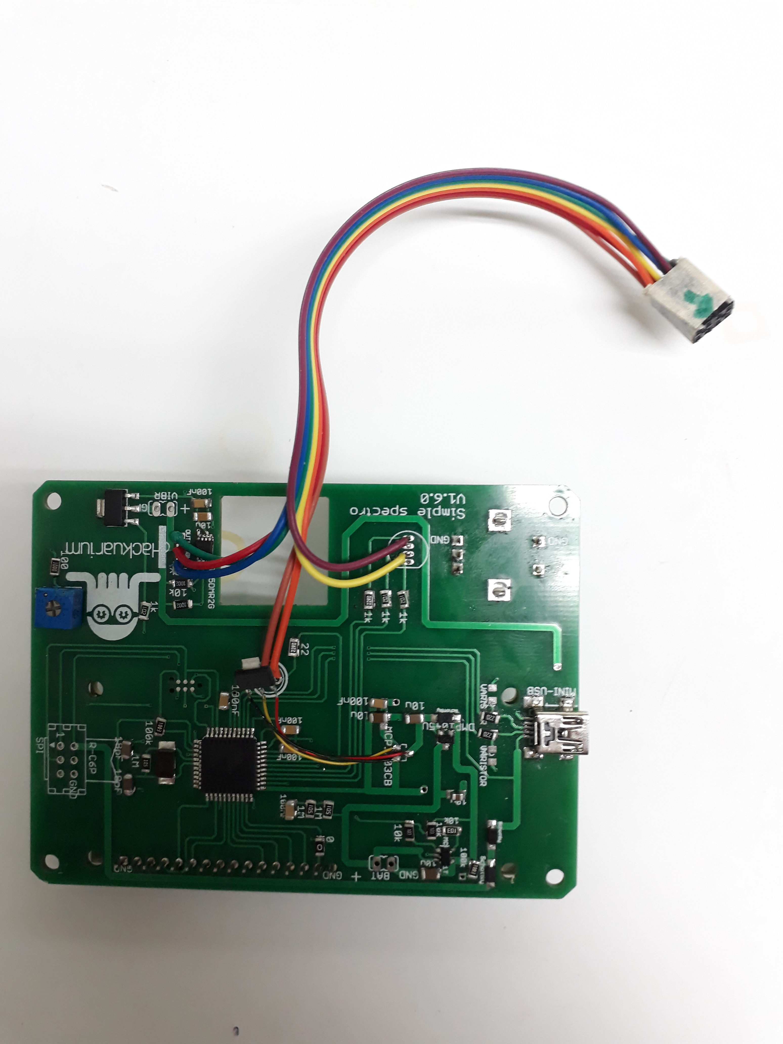
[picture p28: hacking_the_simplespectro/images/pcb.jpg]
the PCB of the spectro-plongeur

<figcaption>The PCB of the spectro-plongeur. See https://github.com/Hackuarium/simple-spectro/tree/master/docs/1-pcb/solder for instructions on how to solder it.</figcaption>
</figure>

## The acrylic parts

The three parts 7.1, 7.2 and 7.3 are cut using a CNC X-Carve 1000mm x 1000mm from Inventables. The 2D drawings can be found in https://github.com/Hackuarium/simple-spectro/tree/master/hacking_the_simplespectro/CAD. Open the .svg files in easel.inventables.com (a free account can be created). This application allows the user to choose the cut settings. In our case, a 2mm spindle was used and the cut settings were: feed rate - 635mm/min, plunge rate - 228.6 m/min, depth per pass - 0.6 mm

<figure>
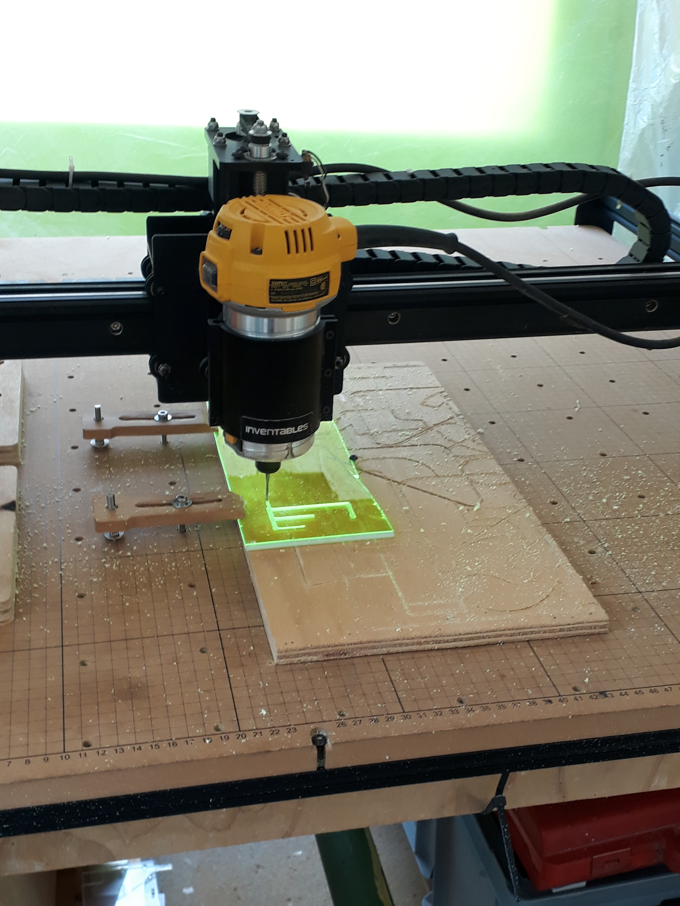
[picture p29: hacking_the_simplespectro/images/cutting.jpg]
Cutting the parts

<figcaption>Cutting acrylic with X-Carve CNC.</figcaption>
</figure>

## Assemble the spectro-plongeur

Connect the LEDs and the receptor with sheath to the right cables of the PCB. The parts are pasted together with multipurpose adhesive liquid silicone. The glue is applied thoroughly in a thin layer on the parts (1 and 2), making sure the glue forms a continuous line on the edges to prevent leaks. Let dry for an hour. Repeat the procedure with the third part. The cables must be well inserted in the channels. The assembly is clenched with tools for drying. The surface near the receptor is polished until it can be distinguished through the acrylic. If necessary, apply a layer of silicone on the junctions on the edge of the spectro-plongeur and let dry again. Immerse it in water for at least an hour (water may seeps in very slowly through small cracks)  to check if it is waterproof. If not, apply another layer of silicone. Finally, solder a 8 pins connection to the spectro-plongeur and the PCB. 

The spectro-plongeur is then ready to be used - see https://github.com/Hackuarium/simple-spectro/blob/master/hacking_the_simplespectro/documentation/using.md.

<figure>
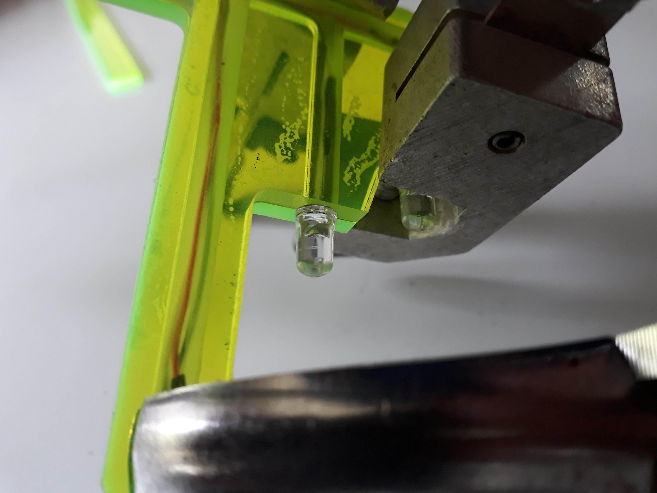
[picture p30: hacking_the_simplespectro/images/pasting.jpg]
Pasting the parts 1 and 2

<figcaption>Pasting parts 1 and 2 with silicone.</figcaption>
</figure>

<figure>
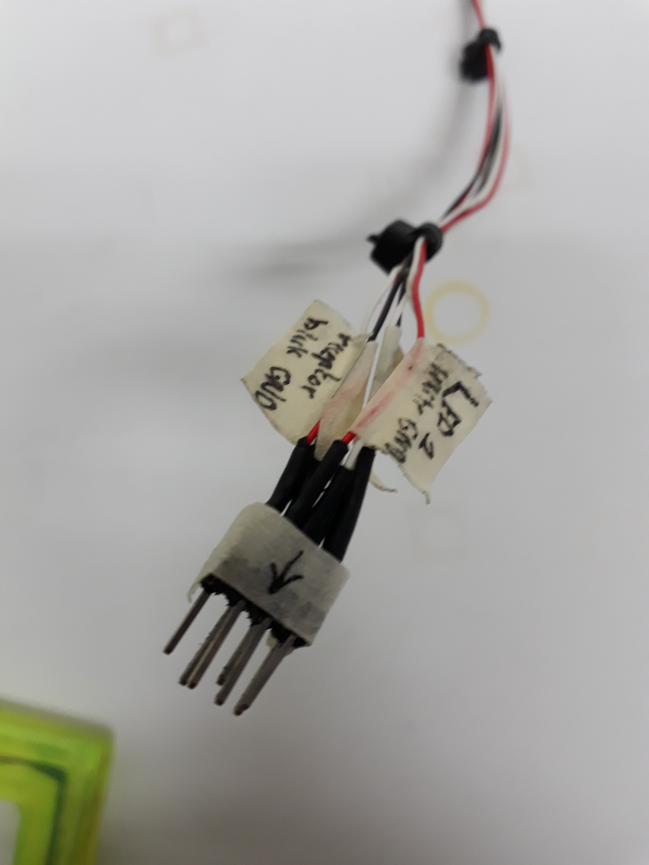
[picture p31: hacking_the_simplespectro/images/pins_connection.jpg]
8 pins connection

<figcaption>8 pins connection of the spectro-plongeur.</figcaption>
</figure>

<figure>
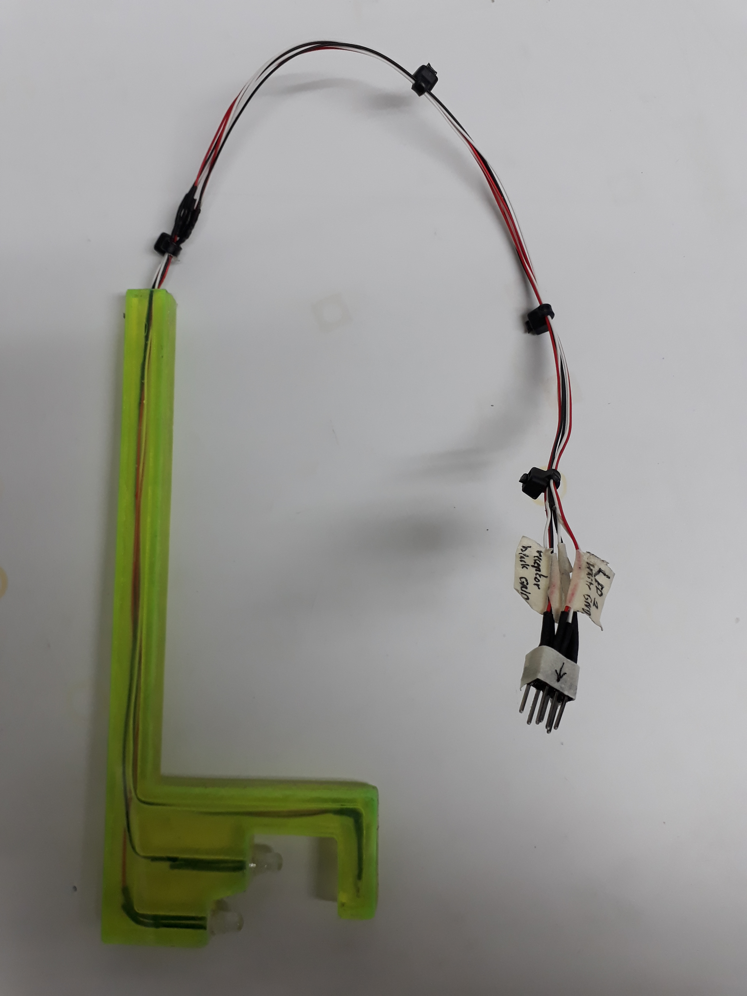
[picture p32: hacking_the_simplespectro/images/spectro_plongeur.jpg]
assembled probe

<figcaption>Assembled probe.</figcaption>
</figure>

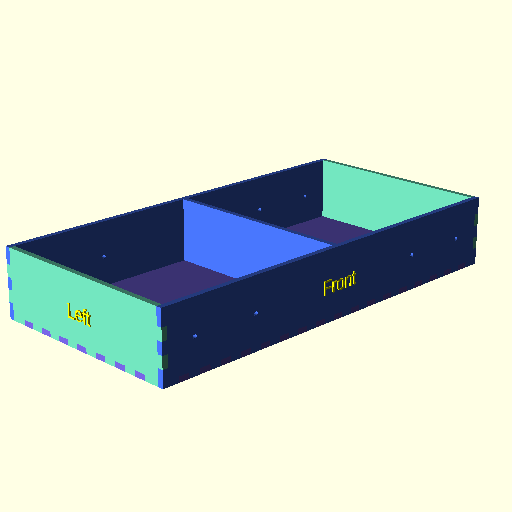
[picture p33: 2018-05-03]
tutorial/openscad/lasercut-box/examples/pivotbox_bottom.png

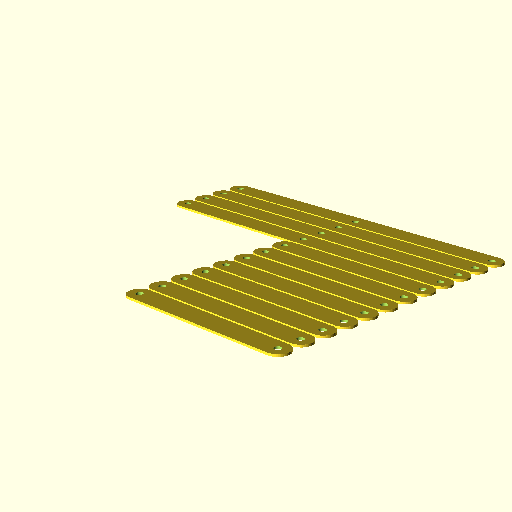
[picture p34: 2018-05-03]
tutorial/openscad/lasercut-box/examples/pivotbox_rods.png

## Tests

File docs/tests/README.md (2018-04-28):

# Expected voltages for USB powered without battery

Testing points are marked on the eagle file and are between ground and the specific point:

* A: 5.01v
* B: 4.78v
* C: 4.55v
* D: 3.35v
* E: 2.92v
* F: 0.23v
* G: 0.35v
* H: 0.86v
* I: 0.86v
* J: 0.05v
* K: 0.00v
* L: 3.25v
* M; 0.81v
* N: 2.90v

# Callibration of the RGB leds

The sensor is able to generate a frequency of maximum 500 kHz and that is directly proportional to the energy of the light.

In order to use the full range of frequency it is important to be at the limit of 500 kHz by changing the 3 resistors that limit the current to the leds.

By default the resistors are 1k.

Example (on D1)

| R red | Red (Hz) | R green | Green (Hz) | R blue | Blue (Hz) | R uv | UV (Hz) |
| ------|----------|---------|------------|--------|-----------|------|---------|
| 1k    | 95240    | 1k      | 185230     | 1k     | 201170    | 22   | 9940 .  |
| 330   | 276500   | 330     | 416200     | 470    | 383320    | 22   | 9940 .  |
| 220   | 383700   |         |            | 330    | 506290    | 22   | 9940 .  |

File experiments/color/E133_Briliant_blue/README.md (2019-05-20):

# E133 - Briliant blue

## Exploratory experiments

The goal is to evaluate the concentration required to have an absorbance of around 0.5.

We took 427.0 mg in 100mL of water.

From this we placed 0.5mL in 100mL.

### 21 mg/L

| Color | Absorbance | Emission |
| ----- | ---------- | -------- |
| Red   | 1.04       |          |
| Green | 0.04       |          |
| Blue  | 0.10       |          |
| UV    |            | 0        |

### 10.5 mg/L

| Color | Absorbance | Emission |
| ----- | ---------- | -------- |
| Red   | 0.61       |          |
| Green | 0.05       |          |
| Blue  | 0.01       |          |
| UV    |            | 8        |

### Conclusions

We need around 9 mg/L to have an absorbance in red of around 0.5.

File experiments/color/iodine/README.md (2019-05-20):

# Determination of the concentration in oxigenated water (H2O2) using potassium iodine (KI)

## Goal

Find appropriate solutions concentrations of H2O2 and KI to realize experiments using the simple-spectro.

**Caution:** H2O2 is dangerous: it is really exothermic when mixed with acid. It can explode. Avoid contact with skin. On the contrary, KI is totally fine, since it is even sometimes ingested for medical purpose.

## Principle

Two solutions are required: a solution of H2O2 and a solution of KI. The goal is to mix them together having an excess of KI so that all the H2O2 reacts and results in iodine, which is brown and can be measured using a spectrophotometer.

## First batch of solutions

We realized solutions at 0.1 M. To do so, we placed 4.15 g (measured using a scale, precision: 0.001g) of KI in a 250 ml calibrated flask and completed with deionized water, agitating well to dissolve all the KI (room temperature is sufficient). Similarly, place 2.5 ml of 30% H2O2 in a 250 ml calibrated flask and complete with deionized water.

To measure the color, we mixed 4ml of the KI solution with 1 ml of the H2O2 solution.

**Measures of absorbance:**

- red: 0.00
- green: 0.04
- blue: 0.06

**Conclusion:** Solutions were not concentrated enough. We tried with solutions 10 times more concentrated.

## Second batch of solutions

4 mL KI 1M
1 mL H2O2 1M

## Second batch of solutions

4 mL KI 0.1M
1 mL H2O2 0.1M
1 mL AcOH 1M

**Measures of absorbance:**

- red: 0.10
- green: 0.54
- blue: 1.66

## Third batch

A : KI 0.1M
B : AcOH 1M
C : H2O2 0.1M
D : H2O

| exp | A   | B   | C     | D      | R   | G   | B   |
| --- | --- | --- | ----- | ------ | --- | --- | --- |
| 1   | 4mL | 1mL | 500uL | 0 uL   |     |     |
| 2   | 4mL | 1mL | 400uL | 100 uL |     |     |
| 3   | 4mL | 1mL | 300uL | 200 uL |     |     |
| 4   | 4mL | 1mL | 200uL | 300 uL |     |     |
| 5   | 4mL | 1mL | 100uL | 400 uL |     |     |
| 6   | 4mL | 1mL | 0uL   | 500 uL |     |     |

### 5 min

E R G B UV
12577193 387718 403065 384133 417
12594548 223065 55675 2758 546
12610603 232675 72691 5427 753
12626255 280567 117289 13706 814
12644618 339650 227652 57634 734
12660371 375441 333788 163714 392
12679335 388637 405498 383777 530

### 10 min

E R G B UV
13061752 389020 407754 385773 402
13078204 156613 18952 386 418
13091850 173585 32390 1134 455
13105797 224915 61675 3716 475
13119242 318763 164851 21973 468
13134092 363637 286491 94578 431
13148340 382483 408947 382763 507

### around 20 min

E R G B UV
13474330 387667 402271 384342 406
13488975 117434 9789 77 363
13502019 138779 18208 395 396
13516167 186529 37383 1424 414
13531117 294999 119511 10251 383
13543759 351437 246161 58623 412
13556101 382648 408938 382256 473

## Kinetic trial with AcOH

A : KI 0.1M
B : AcOH 1M
C : H2O2 0.1M
D : H2O

| exp | A   | B   | C    | D    |
| --- | --- | --- | ---- | ---- |
| 1   | 4mL | 1mL | 60uL | 0 uL |

Kinetic at 23°C shows a fast reaction (5 minutes) followed by a much slower reaction.



## Kinetic trial with H2SO4

A : KI 0.1M
B : H2SO4 1M
C : H2O2 0.1M
D : H2O

| exp | A   | B   | C    | D    |
| --- | --- | --- | ---- | ---- |
| 1   | 4mL | 1mL | 60uL | 0 uL |

In presence of H2SO4 the reaction is much faster.



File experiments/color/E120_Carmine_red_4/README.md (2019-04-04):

# E120 - Carmine red 4

## 12.3 mg in 100mL of water

| Color | Absorbance | Emission |
| ----- | ---------- | -------- |
| Red   | 0.01       |          |
| Green | 0.14       |          |
| Blue  | 0.07       |          |
| UV    |            | 6        |

## 38.4 mg / 100 mL

| Color | Absorbance | Emission |
| ----- | ---------- | -------- |
| Red   | 0.02       |
| Green | 0.43       |
| Blue  | 0.26       |
| UV    |            | -14      |

### Conclusions

We need around 380 mg/L to have an absorbance in red of around 0.5.

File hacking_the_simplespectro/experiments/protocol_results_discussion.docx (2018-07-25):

# Protocol – Results – Conclusion of Experiments

Note: the 1st experiment is not documented since it was mislead and served more as a test to create the protocol for the following experiments, i.e. the 2nd, the 3rd and the 4th ones. In experiments 2 and 3, the LEDs and the receptor are placed outside the bioreactor. In experiment 4, the

- Protocol:
  - Objectives:
    1. Observe the linear relation between concentration and absorbance using the same spectrophotometer but in 2 different configurations
    2. Compare this linear relation for the two methods (R^2 coefficient, std)
    3. Compare the absolute values of absorbance with the 2 methods

Figure 1: settings of spectro 2

  - Material
    4. Distilled water
    5. Recipients
    6. 1mL pipette
    7. Graduated tube
    8. Bioreactor’s recipient
    9. Simple spectro – referred as spectro 1
    10. Spectro plongeur – referred as spectro 2 operated in kinetic mode
    11. USB – micro USB cable
    12. Bioreactor’s container
  - Protocol:
    13. Settings of the spectro 2, see figure 1. Enter “s” in the serial port console of Arduino to see all the parameters.
    14. Measure 300mL with a graduate cylinder and weigh approximately 24mg of colorant Methylene Mx985 (n° 53)
    15. Start with 300mL with a concentration of ~80mg/L (start with 600mL and ~40mg/L for the spectro-plongeur)
    16. Perform measurement of absorbance with the spectro 2. Take a sample to measure the absorbance with the spectro 1 using the 1mL pipette.
    17. Collect the data of light intensity Ii by connecting the devices to the computer. The spectro 2 is in kinetic mode with 5 + 1 = 6 measurements while the spectro 1 is in ‘acquiring sample’ mode with 1+1 = 2 measurements. Less measurements are performed with the spectro 1 since it has a higher reproducibility.
    18. Add 100mL of water (or 50mL if starting with 600mL). Perform points 4 and 5 again until reaching 1000mL. The maximum concentrations are therefore 82.7mg/L and 84.7mg/L which correspond roughly to the upper limit of the domain where the linear relation between absorbance and concentration is observed when using the spectrophotometer.
  - Data and results are available in Results_Azul53_2.xlsx. Christian, from showed me how to use the scale and helped me realize the experiment.
  - Errors
    19. for the concentration: C=C(m,V)=m/V [(mg)/L]=> ΔC=(∂C)/(∂m) (m- m)+(∂C)/(∂V) (V-V)=(Δm)/V ∓ m/(V^2)ΔV=>err_(C-rms) =√(((Δm)/V)^2 +(m/(V^2)ΔV)^2)
    20. for the absorbance: A=A(I_0 , I_i )=log_10 [(I_0)/(I_i)]=>ΔA=1/(log(10)) [(ΔI_0)/(I_0)∓ (ΔI_i)/(I_i)]=>err_(A-rms) =1/(log(10)) √(((ΔI_0)/(I_0))^2 +((ΔI_i)/(I_i))^2)

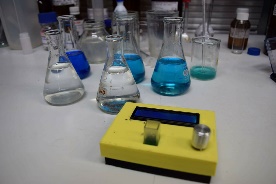
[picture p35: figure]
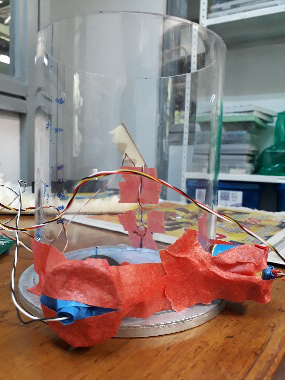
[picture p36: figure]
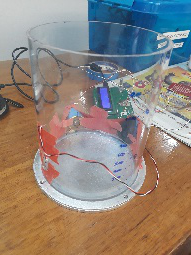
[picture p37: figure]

Figure 2: Spectro 1

Figure 3: Spectro 2 with 2 LEDs with different distances to the receptor in experiments 2 and 3.

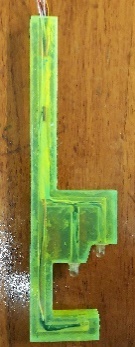
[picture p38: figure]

Figure 3: Spectro 2 - plongeur

  - Notes for experiments 2 and 3:
    21. Spectro 2 – outside version:
      - LED 1 – 120mm = diameter of the cylinder (with 6mm of Plexiglas)
      - LED 2 – 97mm = shorter distance (with 8mm of Plexiglas)
    22. Spectro 2 – inside version
  - Uncertainties
    23. concentration: reading of the scale (+/- 0.1mg) and half of the resolution of the graduated cylinder (+/- 5mL or 0.5mL) each time volume was added to the bioreactor. RSS method for cumulative effect of the errors.
    24. Absorbance: error = 1-time std of the sequence of measurement
- Results of experiment 2
- Results of experiment 3
- Results of experiment 4
- Conclusion experiment 2:
  - The lack of power of the first LED does not allow us to calculate the absorbance (almost all the light is blocked by the medium). Moreover, since the LED is not facing the receptor, less power is emitted in towards it.
  - Linear regression with R^2 = 0.999 (as in https://github.com/Hackuarium/simple-spectro) and R^2 = 0.953 for the spectro 1 and 2 (2nd LED) respectively. However, the responsivity is different: slopes of 0.0063 and 0.0473.
- Conclusion experiment 3:
  - Sometimes, data are not coherent -> perform the sequence again. Can be detected automatically -> the calculated absorbance for the 6 tests must be 0 +/- 0.005 for example
  - Each time |abs.| > 0.01, re-perform the sequence
  - Higher reproducibility of the results of spectro 1 (probably more protected from external light) with R^2 close to 0.999 while for the spectro 2, 0.966 and 0.792 are obtained for the longer and shorter distances respectively. Even though that the power of the light is higher, the results are still not satisfying (in the best case, one would expect to get R^2 = 0.999).
  - Additionally, the offset of the linear regression is reasonably close to 0 only for the spectro 1: its value is -0.0092 in this case, while it reaches 0.43 and 0.66 for the 2 other case. One may also add a constraint of intersection on the linear regression, which however reduces the correlation of determination.
  - For the second LED, which is not directly facing the receptor but is closer to it, the intensity reaching the receptor is lower. Phenomena of reflection and diffusion may cause this loss of power. One could change its direction but then, more reflection at the plexiglass wall would occur. It seems necessary to think of another design, such as the version 2, which will be developed.
- Conclusion experiment 4:
  - In this experiment, we obtain a better linear regression with the spectro 2 thant with the spectro 1 (R^2 = 0.98 for spectro 2 while R^2 = 0.97 with spectro 1)
  - The system of the spectro-plongeur gives satisfying results compared to the previous design and seems to be a better option.
  - The shorter distance between LEDs and receptor leads to smaller standard deviation in the measurement sequence
  - It can be noted that the slope the linear regression for spectro-2 (0.0067) is close to the ones obtained in experiments 2 and 3, with 0.0063 and 0.0065 respectively. Considering the fact that the difference of the length of the light path for spectro-2 is close to the light path.

Yann Meier June 7, 2018

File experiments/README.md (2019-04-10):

# Our laboratory notebook

At hackuarium everything is open-source and the laboratory notebook concerning the spectrophotometer is shown in this folder.

We highlight some representative experiments that you may easily reproduce.

- [Bacteria](bacteria/README.md)
  - [Escherichia Coli](bacteria/escherichia_coli/README.md)
- [Color](color/README.md)
  - [E120 Carmine red 4](color/E120_Carmin_red_4/README.md)
  - [E131 Patent blue V](color/E131_Patent_blue_V/README.md)
  - [E133 Briliant blue](color/E133_Briliant_blue/README.md)
- [Fluorescence](fluorescence/README.md)
  - [Fluorescein](fluorescence/fluorescein/README.md)
- [Kinetc](kinetic/README.md)
  - [Phenolphthalein](kinetic/phenolphthalein/README.md)

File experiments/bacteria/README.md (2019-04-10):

# Bacteria

[Escherichia Coli](escherichia_coli/README.md)

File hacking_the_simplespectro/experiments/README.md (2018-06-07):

This folder contains the protocols and the results (excel spreadsheets) of the experiments lead with the hacked spectro.

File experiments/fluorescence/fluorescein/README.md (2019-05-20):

# Fluorescein

## Exploratory experiments

The goal is to evaluate the concentration required to have an absorbance of around 0.5

We took 14 mg of fluorescein in 100mL of water

### 14 mg/L

| Color | Absorbance | Emission |
| ----- | ---------- | -------- |
| Red   | 0.01       |          |
| Green | 0.43       |          |
| Blue  | 1.79       |          |
| UV    |            | -1358    |

From the previous solution we 0.5mL and bring it to 5mL.

### 1.4 mg/L

| Color | Absorbance | Emission |
| ----- | ---------- | -------- |
| Red   | -0.02      |          |
| Green | 0.14       |          |
| Blue  | 0.95       |          |
| UV    |            | -2878    |

### 0.7 mg/L

| Color | Absorbance | Emission |
| ----- | ---------- | -------- |
| Red   | 0          |          |
| Green | 0.07       |          |
| Blue  | 0.56       |          |
| UV    |            | 2953     |

### Conclusions

An absorbance in blue of around 0.5 is achieved with a concentration of phenolphathlein of 0.7mg/L.
At this concentration the spectrophotometer has a fluorescence of 2953 internal unit.

## CaCl2.2H2O solution

4.64 g/L

## Fluorescence in presence of Ca++

Solution A: fluorescein 1.4 mg/L
Solution B: CaCl2.H2O 4.64 g/L

| A   | B   | H2O | R     | G    | B    | UV   |
| --- | --- | --- | ----- | ---- | ---- | ---- |
| 2   | 0   | 2   | -0.01 | 0.10 | 0.53 | 2237 |
| 2   | 0.5 | 1.5 | -0.01 | 0.11 | 0.55 | 2160 |
| 2   | 1   | 1   | 0     | 0.10 | 0.55 | 2193 |
| 2   | 1.5 | 0.5 | -0.00 | 0.11 | 0.55 | 2265 |
| 2   | 2   | 0   | 0.00  | 0.10 | 0.55 | 2250 |

369mg of CaCl2.2H2O in 2 + 2 mL (2 experiments) (concentration of 92g/L)

| A   | B   | H2O | R     | G    | B    | UV   |
| --- | --- | --- | ----- | ---- | ---- | ---- |
| 2   | 0   | 2   | -0.00 | 0.09 | 0.52 | 2052 |
| 2   | 0   | 2   | -0.00 | 0.11 | 0.53 | 2088 |

### Conclusion

In presence of CaCl2 at high concentration there is no clear evidence of a fluorescence quenching.

## Test with KI

Solution A: fluoresceine 1.4 mg/L
Solution B: KI 10 g/L

| A   | B   | H2O | R    | G    | B    | UV   | UV second experiment |
| --- | --- | --- | ---- | ---- | ---- | ---- | -------------------- |
| 2   | 0   | 2   | 0    | 0.07 | 0.56 | 2953 | 2942                 |
| 2   | 0.5 | 1.5 | 0.01 | 0.07 | 0.58 | 2817 | 2816                 |
| 2   | 1   | 1   | 0.00 | 0.08 | 0.56 | 2603 | 2618                 |
| 2   | 1.5 | 0.5 | 0.00 | 0.07 | 0.57 | 2503 | 2517                 |
| 2   | 2   | 0   | 0    | 0.07 | 0.57 | 2283 | 2243                 |

https://docs.google.com/spreadsheets/d/1UuKFU8COCiJQ89IAYm6FFq3e50cZny3WdU-MUHwkeag/edit?usp=sharing

### Conclusions

It seems that we observe a fluorescence quenching but other factors like influence of pH should be checked.
Literature shows that this kind of experiment is done in presence of 0.1M of KOH.

Check page 12 of : https://www.chem.uzh.ch/dam/jcr:571775eb-8b0e-4930-8aa4-ad0da5c11aec/FluorescenceQuenching_HS16.pdf

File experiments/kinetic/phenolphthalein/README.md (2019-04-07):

# Experience with phenolphthalein

- [2019-04-06: Kinetic experiment](20190406)
- Example of protocol in french [pdf](Phenolphtalein_FR.pdf) [docx](Phenolphtalein_FR.docx)

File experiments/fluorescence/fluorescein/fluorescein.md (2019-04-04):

# Test of solution of fluorescein

## Goal

Check the absorbance and fluorescence of a solution of fluorescein in order to find the lowest concentration required to have a high fluorescence.

## Results

### Spectro 1

| Concentration [µg/L] | E    | R      | G     | B     | UV    |
| -------------------- | ---- | ------ | ----- | ----- | ----- |
| 14                   | 0.25 | 0.008  | 0.298 | 1.743 | 13977 |
| 7                    | 0.47 | 0.012  | 0.213 | 1.642 | 35406 |
| 1.4                  | 0.68 | 0.005  | 0.088 | 1.036 | 66273 |
| 0.7                  | 0.89 | 0.030  | 0.053 | 0.630 | 55499 |
| 0.35                 | 1.11 | -0.001 | 0.030 | 0.340 | 37857 |
| 0.14                 | 1.41 | 0.113  | 0.195 | 0.164 | 18380 |
| 0.07                 | 1.63 | 0.007  | 0.014 | 0.073 | 10000 |

### Spectro 2

| Concentration [µg/L] | E    | R      | G      | B     | UV    |
| -------------------- | ---- | ------ | ------ | ----- | ----- |
| 14                   | 0.24 | 0.005  | 0.294  | 1.738 | 15022 |
| 7                    | 0.48 | 0.011  | 0.208  | 1.641 | 35132 |
| 1.4                  | 0.78 | 0.003  | 0.085  | 1.038 | 69277 |
| 0.7                  | 1.02 | 0.027  | 0.048  | 0.631 | 56721 |
| 0.35                 | 1.26 | -0.002 | 0.025  | 0.339 | 38510 |
| 0.14                 | 1.51 | 0.109  | 0.172  | 0.166 | 18355 |
| 0.07                 | 1.77 | 0.007  | 0.018  | 0.081 | 10121 |
| 0.014                | 2.03 | 0.003  | -0.006 | 0.014 | 2019  |
| 0.0014               | 2.27 | -0.006 | -0.014 | 0.003 | 110   |
| 0                    | 6.71 | 0.004  | 0.002  | 0.000 | 16    |
| 0.0014               | 6.96 | -0.001 | -0.013 | 0.007 | 110   |
| 0                    | 7.18 | 0.011  | 0.012  | 0.008 | 0     |
| 0.0014               | 7.39 | -0.006 | -0.015 | 0.002 | 108   |
| 0                    | 7.63 | 0.009  | 0.010  | 0.007 | 11    |
| 0.0014               | 7.86 | -0.008 | -0.015 | 0.001 | 105   |

https://docs.google.com/spreadsheets/d/1HtbmLdVMgEYo-ZQjiFXmoGVFPik7BkEx7frhzuUpo_E/edit?usp=sharing

## Conclusions

We are able to detect 1.4µg per liter of fluorescein.

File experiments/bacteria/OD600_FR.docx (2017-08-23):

# Introduction

L’OD600 est une mesure utilisée en biologie, qui permet de représenter une croissance d’une culture de bactéries sur plusieurs heures. Il s’agit de mesurer l’absorbance de la suspension bactérienne à 600nm, qui doit être caractérisée par 3 phases distinctes :

- « lag phase » : les bactéries se préparent à se multiplier, on observe donc une absorbance quasi constante pendant la première heure.
- « log phase » : une croissance exponentielle du nombre de bactéries, l’absorbance augmente donc fortement pendant cette période.
- « stationnary phase » : phase pendant laquelle le taux de croissance/mort se compensent, la quantité de bactérie stagne et donc l’absorbance ne varie pas ou peu.

On propose ici d’étudier la bactérie E. Coli et d’essayer de mesurer l’absorbance à une longueur d’onde différente de la conventionnelle 600nm. En effet, le choix du 600nm est un choix « historique » mais tout autre choix de longueur d’onde compris entre 300 et 800nm devrait fonctionner.

# Expérience

Préparation du milieu de culture :

- On compte environ 20g de poudre LB pour 1 litre d’eau. Pour cette expérience, on va donc dissoudre 2g de poudre dans 100g d’eau. Bien agiter.
- Faire chauffer la solution à environ 100 °C pendant 15min pour bien la stériliser et faciliter la dissolution de la poudre.
- Laisser refroidir avant de l’utiliser. Verser ensuite le medium dans la cuvette du spectrophotomètre.

Pour le spectrophotomètre, on vise une mesure toutes les 30min, régler donc le temps inter-expérience à 1790s. Effectuer le blanc avec le LB medium avant d’y ajouter la souche bactérienne. Le choix de la longueur d’onde (R,G ou B) est libre. Avec un ordinateur, il est possible de récupérer les données des 3 couleurs et de pouvoir comparer les 3 directement.

Préparation de la suspension :

- A l’aide d’une pipette pasteur stérilisée, prélever une souche de E. Coli et la déposer dans la cuvette du spectrophotomètre.
- Régler l’incubateur sur 37 °C et 150rpm. Laisser incuber pendant la nuit, et revenir le lendemain pour noter les résultats. Une durée de 10h est suffisante pour distinguer les 3 phases.

Temps(s) | Absorbance

Tracer la droite sur Excel ou alors directement sur papier millimétré :

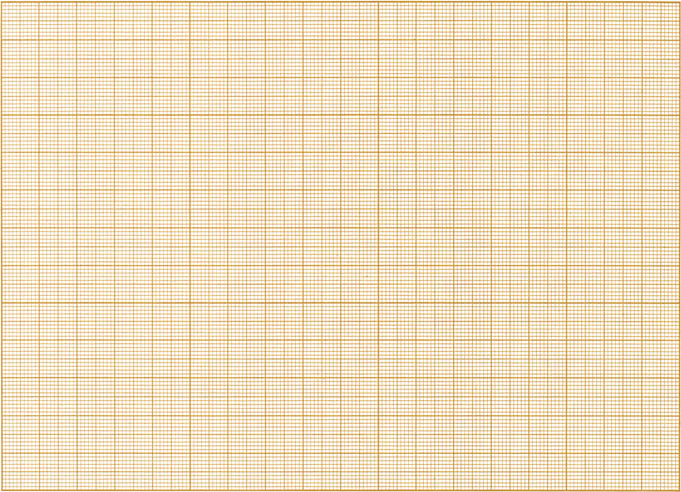
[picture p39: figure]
Résultat de recherche d'images pour "papier millimétré canson a imprimer"

# Analyse

Arrivez-vous à bien distinguer les 3 phases typiques de la croissance bactérienne ?

Pourquoi ne peut-on pas en revanche effectuer un « OD250 », c’est-à-dire une mesure de l’OD dans l’UV ?

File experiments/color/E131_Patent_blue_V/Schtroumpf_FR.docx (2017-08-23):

# Introduction

Le bleu patenté V est un colorant alimentaire qu’on retrouve dans l’industrie alimentaire, malgré les suspicions d’être cancérigène. Pour tous les additifs alimentaires, on retrouve des normes journalières fixées par l’union européenne qu’on nomme DJA (Dose Journalière Admissible). Il s’agit d’un seuil, souvent exprimé en mg/kg, qui exprime la quantité de substance qui peut être ingérée quotidiennement sans risque de répercussion sur la santé.

Nous allons déterminer si la quantité de bleu patenté V présent dans les bonbons Haribo « Schtroumpfs » n’est pas trop élevée par rapport à la quantité régulée par l’UE.

# Expérience

Préparation du bonbon :

- Prendre un schtroumpf (couper le chapeau s’il n’est pas également bleu) et le découper en plusieurs morceaux pour préparer sa dissolution
- Prendre ce dernier, et le dissoudre dans environ 30mL d’eau chaude.
- Verser le tout dans un autre récipient et ajouter 20g d’eau pour arriver à 50mL d’eau.

On va ensuite préparer une droite d’étalonnage du bleu patenté V. Pour ceci, on va préparer 5 solutions de concentrations 2,4,6,8 et 10x10⁻⁶ mol/L, et on mesure leur absorbance respective.

- Commencer par préparer une solution appelée S0, de concentration 10⁻⁴ mol/L.
- Pour ceci, dissoudre 0.0058g de bleu patenté dans 100mL d’eau.
- Préparer S1 en diluant cette solution à 1 :10 (on peut prendre 1g de S0 et ajouter 9g d’eau).
- Préparer S2 en diluant 5g de S1 avec 1.25g d’eau.
- Préparer S3 en diluant 4g de S1 avec 2.66g d’eau.
- Préparer S4 en diluant 3g de S1 avec 4.5g d’eau.
- Préparer S5 en diluant 2g de S1 avec 8g d’eau.

Solution | S5 | S4 | S3 | S2 | S1
Concentration [mol/L] | 2x10⁻⁶ | 4x10⁻⁶ | 6x10⁻⁶ | 8x10⁻⁶ | 10x10⁻⁶
Absorbance [UA]

On trace ensuite la droite sur papier millimétré :

Résultat de recherche d'images pour "papier millimétré canson a imprimer"

Pour les plus avancés, calculer la droite de régression ainsi formée par ces points.

On rappelle qu’elle est de la forme y = ax + b avec a = cov(x,y)∕s_x^2 et b = y - a x .

On donne les formules suivantes :

Trouver alors la concentration en mol/L du bleu patenté V dans la solution de 50mL grâce à la droite d’étalonnage.

# Analyse

Déterminer la masse de bleu patenté V contenu dans un bonbon. On donne la masse molaire du bleu patenté : M = 580 g/mol

Combien de bonbons par jour un adulte de 70kg peut-il manger si on veut respecter la DJA, sachant que celle-ci vaut 2.5mg/kg ? La quantité présente dans ces bonbons est-elle correcte selon vous ?

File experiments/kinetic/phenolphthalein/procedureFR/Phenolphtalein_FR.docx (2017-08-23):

# Introduction

La phénolphtaléine est un indicateur coloré, c’est-à-dire un composé qui change de couleur selon le pH de son environnement, qui se décolore lentement en milieu très basique ( pH >12) selon la réaction P^(2-) +OH^(-) → POH^(3-) .

On propose ici de vérifier que la loi qui régit cette réaction v=k_1 [P^(2-) ]^m [NaOH]^n est bien d’ordre 1 par rapport aux 2 réactifs, c’est-à-dire m=n=1 .

Dans un milieu très basique, on note que la concentration de OH^(-) est très élevée, bien plus que celle de phénolphtaleine. Nous avons donc une réaction de pseudo-ordre 1 v=k_2 [P^(2-) ]^m car on peut considérer [OH^(-) ] est constante, avec k_2 =k_1 [NaOH]^n .

La quantité de P²⁻ est linéaire par rapport à l’absorbance de la solution à 550nm.

On peut alors en conclure que :

- Si la réaction est d’ordre 1 par rapport à la phénolphtaleine, alors le graphe du temps vs ln [A] sera linéaire, de pente -k_2 .
- Si la réaction est d’ordre 1 par rapport aux ions hydroxyde, on a alors k_1 =k_2 /[NaOH] et on peut vérifier que k_2 /[NaOH] reste constant à différentes concentrations initiales de NaOH.

# Expérience

La concentration de phénolphtaléine n’est pas importante dans ce TP, mais elle doit être suffisamment petite pour que NaOH soit en excès.

Préparation des solutions stocks :

- Solution de 0.50M NaOH : peser 2g de NaOH et les dissoudre dans 100g d’eau.
- Solution de phénolphtaléine 0.6% : dissoudre 47mg de phénolphtaléine dans 7.42g d’éthanol.
- Solution de 0.50M NaCl : peser 1.463g de NaCl et les dissoudre dans 50g d’eau.

Remplir la cuvette de solution de NaOH 0.50M et ajouter une goutte de solution de phénolphtaléine. Agiter pour mélanger. On mesure alors l’absorbance dans le vert à une cadence de 1 mesure/10s (on rappelle que le temps de mesure du spectrophotomètre étant d’environ 10s, on arrive donc à 1 mesure/20s).

Expérience 1
Temps (s)
Absorbance
ln(A)

Tracer le graphe ainsi obtenu sur papier millimétré et vérifier s’il s’agit d’une droite.

Déterminer la pente de la droite pour obtenir la constante de vitesse k_2

Résultat de recherche d'images pour "papier millimétré canson a imprimer"

On va répéter l’expérience avec deux autres concentrations de NaOH pour déterminer l’ordre de ce réactif.

Pour l’expérience 2, on va utiliser une solution de 0.3M NaOH en prélevant 30g de la solution stock, et en y ajoutant 20g de la solution de NaCl.

Pour l’expérience 3, on va utiliser une solution de 0.1M NaOH en prélevant 10g de la solution stock et en y ajoutant 40g de la solution de NaCl.

Expérience 2
Temps (s)
Absorbance
ln(A)

Expérience 3
Temps (s)
Absorbance
ln(A)

# Analyse

Pourquoi les mesures d’absorbance ont été réalisées dans le vert ?

Quel est l’ordre de la réaction par rapport à la phénolphtaléine ?

Calculez maintenant k_2 /[NaOH] , [NaOH] étant la concentration initiale, pour les expériences 1, 2 et 3, et vérifiez que ces quantités soient à peu près égales.

Quel est l’ordre de la réaction par rapport aux ions hydroxydes ?

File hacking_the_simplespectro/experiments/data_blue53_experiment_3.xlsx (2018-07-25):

 | Experiment 3 |  |  |  |  |  |  |  |  |  |  |  |  |  |  |  |  |  |  |  |  |  |  |  |  |  |  |  |  |  | Uncertainty
numero | Volume [mL] | concentration [mg/L] | Measurements |  |  |  |  |  |  |  |  |  |  |  |  |  |  |  |  |  |  |  |  |  |  |  |  |  |  |  | quantity | abs. uncertainty | units | notes
 |  |  | Spectro 1 |  |  |  |  | Spectro 2 |  |  |  |  |  |  |  |  |  |  |  |  |  |  |  |  |  |  |  |  |  |  | mass of colorant | 0.1 | mg | Uncertainty of the reading
 |  |  | blue |  |  |  |  | blue 1 |  |  |  |  |  |  |  |  |  |  | blue 2 (UV) |  |  |  |  |  |  |  |  |  |  |  | volume of water | 5 | mL | half of the resolution of the graduated cylinder
 |  |  | I blank | I test | Avg | Abs. calculated | Abs. reading | I blank | I test 1 | I test 2 | I test 3 | I test 4 | I test 5 | Avg | std | error | Abs. calculated | Abs. reading | I blank | I test 1 | I test 2 | I test 3 | I test 4 | I test 5 | Avg | std | error | Abs. calculated | Abs. reading |  | Concentration uncertainty [mg/L]
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

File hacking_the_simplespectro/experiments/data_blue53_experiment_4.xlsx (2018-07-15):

 | Experiment 4 |  |  |  |  |  |  |  |  |  |  |  |  |  |  |  |  |  |  |  |  |  |  |  |  |  |  |  |  |  |  | Uncertainty |  |  |  |  | mm
numero | Volume [mL] | concentration [mg/L] | Measurements |  |  |  |  |  |  |  |  |  |  |  |  |  |  |  |  |  |  |  |  |  |  |  |  |  |  |  |  | quantity | abs. uncertainty | units | notes | thickness1 | 10
 |  |  | Spectro 1 |  |  |  |  | Spectro 2 |  |  |  |  |  |  |  |  |  |  |  |  |  |  |  |  |  |  |  |  |  |  |  | mass of colorant | 0.1 | mg | Uncertainty of the reading | thickness2.1 | 10.5
 |  |  | blue |  |  |  |  | blue 1 |  |  |  |  |  |  |  |  |  |  | blue 2 / UV |  |  |  |  |  |  |  |  |  |  |  |  | volume of water | 5 | mL | half of the resolution of the graduated cylinder
 |  |  | I blank | I test | Avg | Abs. calculated | Abs. reading | I blank | I test 1 | I test 2 | I test 3 | I test 4 | I test 5 | Avg | std | error | Abs. calculated | Abs. reading | I blank | I test 1 | I test 2 | I test 3 | I test 4 | I test 5 | Avg | std | error | Abs. calculated | Abs. reading | Abs. diff. | error | Concentration uncertainty [mg/L]
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

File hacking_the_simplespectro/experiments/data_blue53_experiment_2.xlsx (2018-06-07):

 | Experiment 2 |  |  |  |  |  |  |  |  |  |  |  |  |  |  |  |  |  |  |  |  | Uncertainty
numero | Volume [mL] | concentration [mg/L] | Measurements |  |  |  |  |  |  |  |  |  |  |  |  |  |  |  |  |  |  | quantity | abs. uncertainty | units | notes
 |  |  | Spectro 1 |  |  |  |  | Spectro 2 |  |  |  |  |  |  |  |  |  |  |  |  |  | mass of colorant | 0.1 | mg | Uncertainty of the reading
 |  |  | blue |  |  |  |  | blue 1 |  |  |  |  |  |  | blue 2 (UV) |  |  |  |  |  |  | volume of water | 5 | mL | half of the resolution of the graduated cylinder
 |  |  | I blank | I test | Avg | Abs. calculated | Abs. reading | I blank | I test | Avg | std | error | Abs. calculated | Abs. reading | I blank | I test | Avg | std | error | Abs. calculated | Abs. reading | Concentration uncertainty [mg/L]
0 | 0 |  | 203129 | 203176 | 203152.5 | 0 | 0 | 399 | 394 | 1182.666667 | 17.09580845 |  |  | "0.00" | 142401 | 142593 | 144643 | 31.144823 |  |  | "0.00" | 0
1 | 300 | 0 | 260157 | 259935 | 260046 | 0 |  |  |  | 338.3333333 | 8.57126984 | 0 | 0 | "0.00" |  |  | 371817 | 572.3512907 | 0 | 0 | "-0.00" | 0
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

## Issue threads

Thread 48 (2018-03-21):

### ISSUE TITLE
Turn off LEDs to enhance power savings

### ISSUE THREAD

**Issue by oliemery** [Hackuarium/simple-spectro#48]
Since the LEDs are not visible from the end user, they could be turned off (in particular during sleep) to save power and enhance battery life.
The LEDs are useful for debugging but not used/visible for the assembled version of the spectro. In case the light from these LEDs go through the cuvette (as it is the case with the laser-cut version without a case around the lower part of the cuvette), they may affect the readings in different ways since the colors of the LEDs while change whether the spectro is charging or not via usb for example (although I haven't tested for these effects I could see light through the cuvette in sleep mode in the dark)

**Comment by lpatiny** [comment]
Indeed the leds are useless and they are there in this first release. The new version do not have leds anymore.

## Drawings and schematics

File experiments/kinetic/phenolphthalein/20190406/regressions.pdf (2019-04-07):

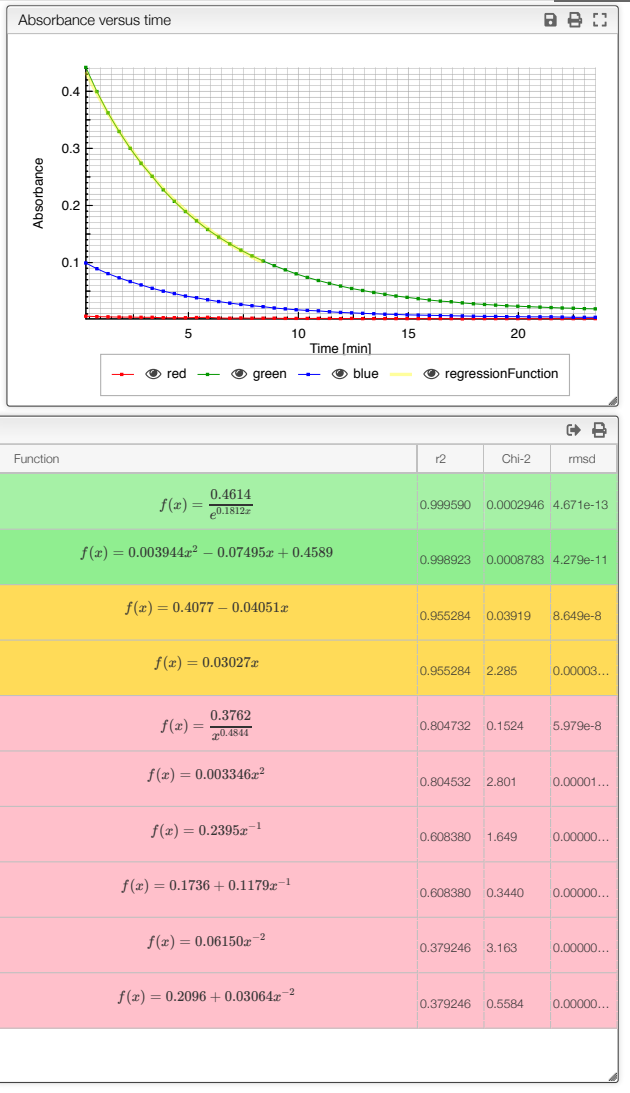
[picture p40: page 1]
Function; Chi-2; rmsd; Time [min]; Absorbance; red; green; blue; regressionFunction

Absorbance versus time

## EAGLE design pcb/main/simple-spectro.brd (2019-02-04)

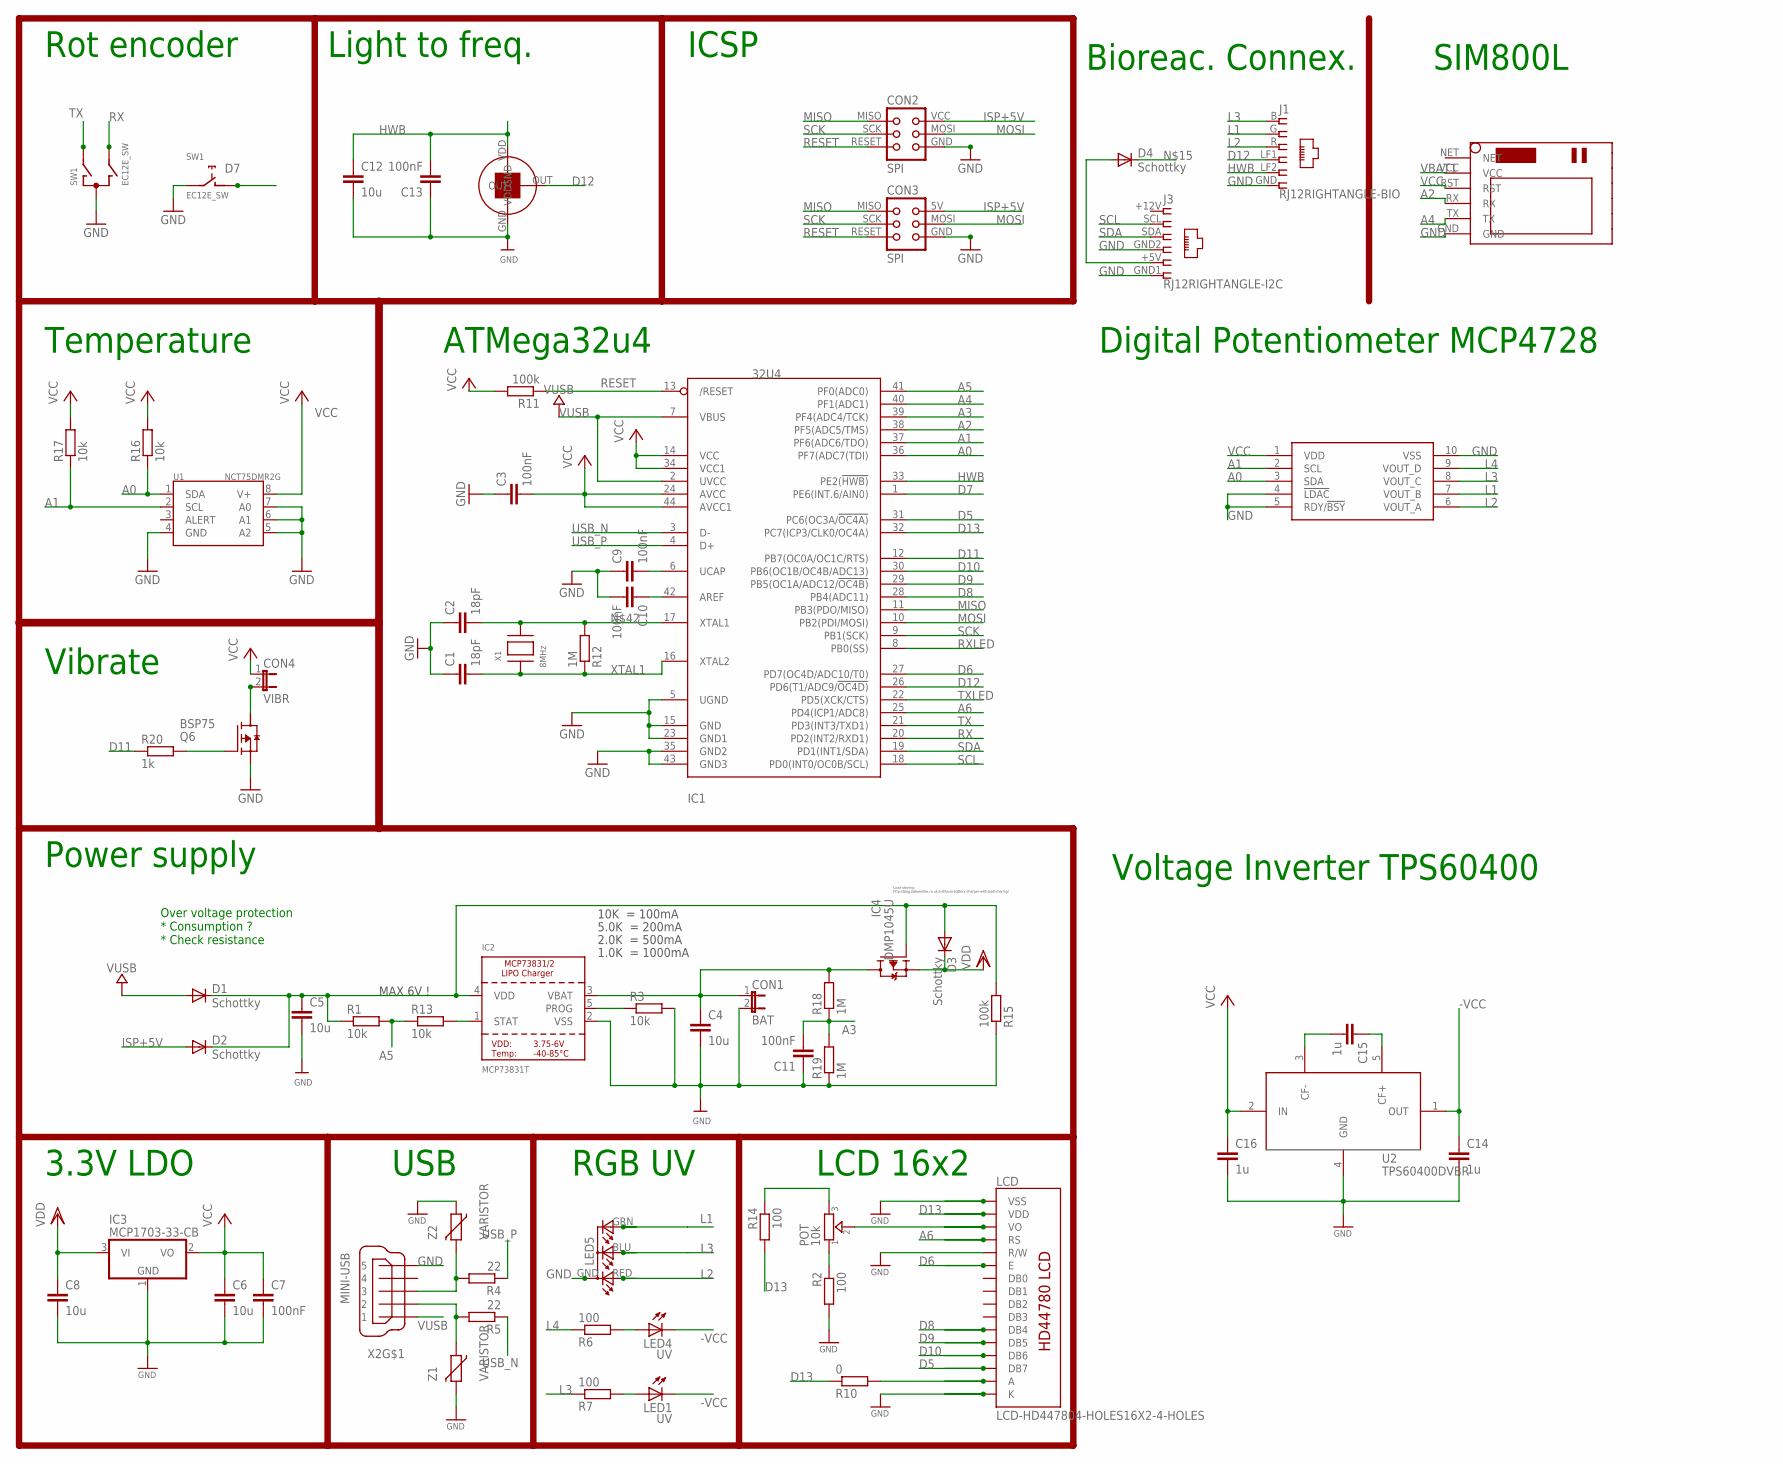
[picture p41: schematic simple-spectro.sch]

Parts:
C1, C2: 18pF; C0805K; MPN 77-VJ1206A180JXXPBC; LCSC C1797
C3, C7, C9, C10, C11, C13: 100nF; C0805K; MPN 80-C1206C104K5R; LCSC C49678
C4, C5, C6, C8, C12: 10u; C0805K; MPN 77-VJ1206V106ZXQTBC; LCSC C15850
C14, C15, C16: 1u; C0805K; MPN 77-VJ1206V106ZXQTBC; LCSC C15850
CON1: BAT; JP1
CON2: SPI; TINYISP
CON3: SPI; TC2030-MCP-NL
CON4: VIBR; JP1
D1, D2, D3, D4: Schottky; SOD123; MPN 621-1N5819HW-F; LCSC C82544
IC1: 32U4; TQFP44; MPN 556-ATMEGA32U4RC-AU; LCSC C44854
IC2: MCP73831T; SOT23-5; MPN 579-MCP73831T-3ACIOT; LCSC C14879
IC3: MCP1703-33-CB; SOT23; LCSC C53352
IC4: DMP1045U; SOT-23; MPN 621-DMP1045U-7; LCSC C110499
J1: RJ12RIGHTANGLE-BIO; RJ12-RIGHTRANGE-RGB
J3: RJ12RIGHTANGLE-I2C; RJ12-RIGHTANGLE-I2C
LCD: LCD-HD447804-HOLES16X2-4-HOLES; LCD-16X2-4HOLES
LED1, LED4: UV; LED5MM
LED5: RGB-COMMON-CATHODE; LED-TRICOLOR-THROUGHHOLE
POT: 10k; TRIMMER_3362P
Q6: BSP75; PG-SOT-223
R1, R3, R13, R16, R17: 10k; R0805; LCSC C17414
R2, R6, R7, R14: 100; R0805; LCSC C17408
R4, R5: 22; R0805; LCSC C17561
R10: 0; R0805; LCSC C17477
R11, R15: 100k; R0805; MPN RC1206FR-07100KL; LCSC C17407
R12, R18, R19: 1M; R0805; LCSC C17514
R20: 1k; R0805; LCSC C17513
SW1: EC12E_SW; ALPS_EC12E_SW
U1: NCT75DMR2G; MSOP8; LCSC C94387
U2: TPS60400DVBR; SOT23-5
U$1: SIM800LMODULE
U$4: MCP4728; MSOP10
U$7: TSL237
X1: 8MHz; NX6035; MPN 729-F60800010; LCSC C122522
X2: MINI-USB; 32005-201; MPN 649-10033526-N3212LF; LCSC C46391
Z1, Z2: VARISTOR; CT/CN0603; LCSC C126845

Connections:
1: J3.+12V (1)
-VCC: C14.1, LED1.K (C), LED4.K (C), U2.1 (OUT)
A0: IC1.36 (PF7(ADC7(TDI)), R16.1, U1.1 (SDA), U$4.3 (SDA)
A1: IC1.37 (PF6(ADC6/TDO)), R17.1, U1.2 (SCL), U$4.2 (SCL)
A2: IC1.38 (PF5(ADC5/TMS)), U$1.RX
A3: C11.2, IC1.39 (PF4(ADC4/TCK)), R18.1, R19.2
A4: IC1.40 (PF1(ADC1)), U$1.TX
A5: IC1.41 (PF0(ADC0)), R1.2, R13.1
A6: IC1.25 (PD4(ICP1/ADC8)), LCD.4 (RS)
AREF: C10.1, IC1.42 (AREF)
D5: IC1.31 (PC6(OC3A/!OC4A)), LCD.14 (DB7)
D6: IC1.27 (PD7(OC4D/ADC10/T0)), LCD.6 (E)
D7: IC1.1 (PE6(INT.6/AIN0)), SW1.D (1)
D8: IC1.28 (PB4(ADC11)), LCD.11 (DB4)
D9: IC1.29 (PB5(OC1A/ADC12/!OC4B)), LCD.12 (DB5)
D10: IC1.30 (PB6(OC1B/OC4B/ADC13)), LCD.13 (DB6)
D11: IC1.12 (PB7(OC0A/OC1C/RTS)), R20.1
D12: IC1.26 (PD6(T1/ADC9/!OC4D)), J1.LF1 (4), U$7.OUT
D13: IC1.32 (PC7(ICP3/CLK0/OC4A)), LCD.2 (VDD), R10.1, R14.2
GND: C1.1, C2.1, C3.1, C4.2, C5.2, C6.2, C7.2, C8.2, C9.1, C10.2, C11.1, C12.2, C13.1, C14.2, C16.2, CON1.2, CON2.GND, CON3.GND, IC1.5 (UGND), IC1.15 (GND), IC1.23 (GND1), IC1.35 (GND2), IC1.43 (GND3), IC2.2 (VSS), IC3.1 (GND), J1.GND (6), J3.GND1 (6), J3.GND2 (4), LCD.1 (VSS), LCD.5 (R/W), LCD.16 (K), LED5.GND (A2), Q6.3 (S), R2.2, R3.2, R15.1, R19.1, SW1.C, SW1.E (2), U1.4 (GND), U1.5 (A2), U1.6 (A1), U1.7 (A0), U2.4 (GND), U$1.GND, U$4.4 (!LDAC), U$4.5 (RDY/!BSY), U$4.10 (VSS), U$7.GND, X2.5, Z1.2, Z2.1
HWB: C12.1, C13.2, IC1.33 (PE2(!HWB)), J1.LF2 (5), U$7.VDD
ISP+5V: CON2.VCC, CON3.5V (VCC), D2.A
L1: J1.G (2), LED5.GRN (CGREEN), U$4.7 (VOUT_B)
L2: J1.R (3), LED5.RED (CRED), U$4.6 (VOUT_A)
L3: J1.B (1), LED5.BLU (CBLUE), R7.1, U$4.8 (VOUT_C)
L4: R6.1, U$4.9 (VOUT_D)
MISO: CON2.MISO, CON3.MISO, IC1.11 (PB3(PDO/MISO))
MOSI: CON2.MOSI, CON3.MOSI, IC1.10 (PB2(PDI/MOSI))
unnamed: C9.2, IC1.6 (UCAP)
unnamed: LCD.3 (VO), POT.2
unnamed: D4.A, J3.+5V (5)
unnamed: POT.1, R2.1
unnamed: IC2.1 (STAT), R13.2
unnamed: IC2.5 (PROG), R3.1
unnamed: LED4.A, R6.2
unnamed: Q6.1 (G), R20.2
unnamed: LED1.A, R7.2
unnamed: LCD.15 (A), R10.2
unnamed: POT.3, R14.1
unnamed: CON4.2, Q6.2 (D)
unnamed: C5.1, D1.C, D2.C, D3.A, D4.C, IC2.4 (VDD), IC4.1 (G), R1.1, R15.2
unnamed: C15.2, U2.3 (CF-)
unnamed: C15.1, U2.5 (CF+)
unnamed: C2.2, IC1.17 (XTAL1), R12.2, X1.P$2
RESET: CON2.RESET, CON3.RESET, IC1.13 (/RESET), R11.1
RX: IC1.20 (PD2(INT2/RXD1)), SW1.B
RXLED: IC1.8 (PB0(SS))
SCK: CON2.SCK, CON3.SCK, IC1.9 (PB1(SCK))
SCL: IC1.18 (PD0(INT0/OC0B/SCL)), J3.SCL (2)
SDA: IC1.19 (PD1(INT1/SDA)), J3.SDA (3)
TX: IC1.21 (PD3(INT3/TXD1)), SW1.A
TXLED: IC1.22 (PD5(XCK/CTS))
USBC_N: R5.2, X2.2, Z1.1
USBC_P: R4.2, X2.3, Z2.2
USB_N: IC1.3 (D-), R5.1
USB_P: IC1.4 (D+), R4.1
VBAT1: C4.1, CON1.1, IC2.3 (VBAT), IC4.3 (D), R18.2, U$1.VCC
VCC: C3.2, C6.1, C7.1, C16.1, CON4.1, IC1.14 (VCC), IC1.24 (AVCC), IC1.34 (VCC1), IC1.44 (AVCC1), IC3.2 (VO), R11.2, R16.2, R17.2, U1.8 (V+), U2.2 (IN), U$1.RST, U$4.1 (VDD)
VDD: C8.1, D3.C, IC3.3 (VI), IC4.2 (S)
VUSB: D1.A, IC1.2 (UVCC), IC1.7 (VBUS), X2.1
XTAL1: C1.2, IC1.16 (XTAL2), R12.1, X1.P$1

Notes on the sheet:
USB
ICSP
ATMega32u4
LCD 16x2
Rot encoder
3.3V LDO
10K = 100mA
5.0K = 200mA
2.0K = 500mA
1.0K = 1000mA
MAX 6V !
Load sharing: http://blog.zakkemble.co.uk/a-lithium-battery-charger-with-load-sharing/
RGB UV
Over voltage protection * Consumption ? * Check resistance
Light to freq.
Power supply
Temperature
Vibrate
Voltage Inverter TPS60400
Digital Potentiometer MCP4728
SIM800L
Bioreac. Connex.

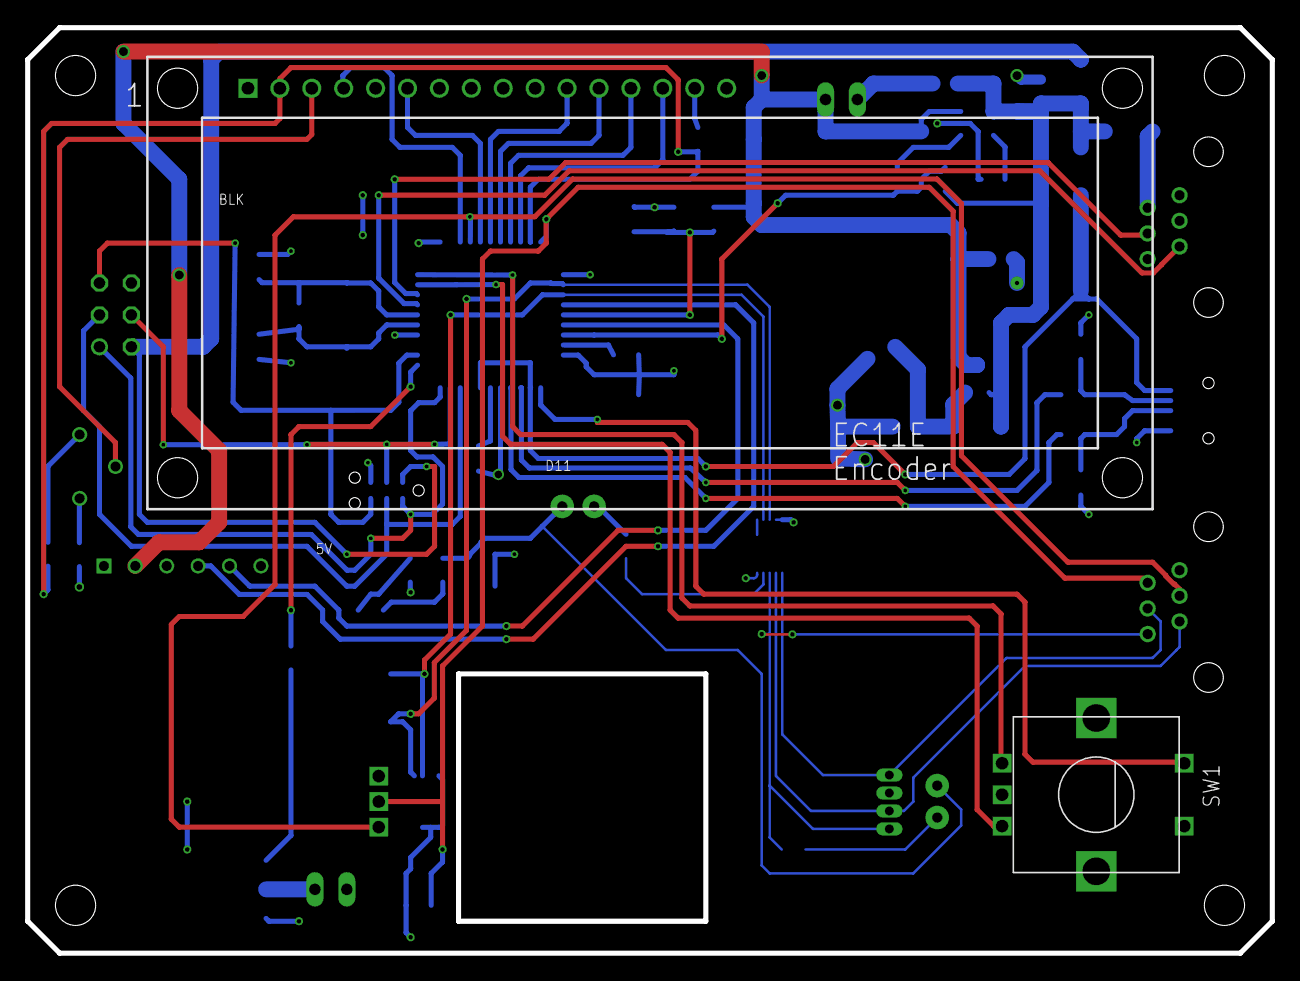
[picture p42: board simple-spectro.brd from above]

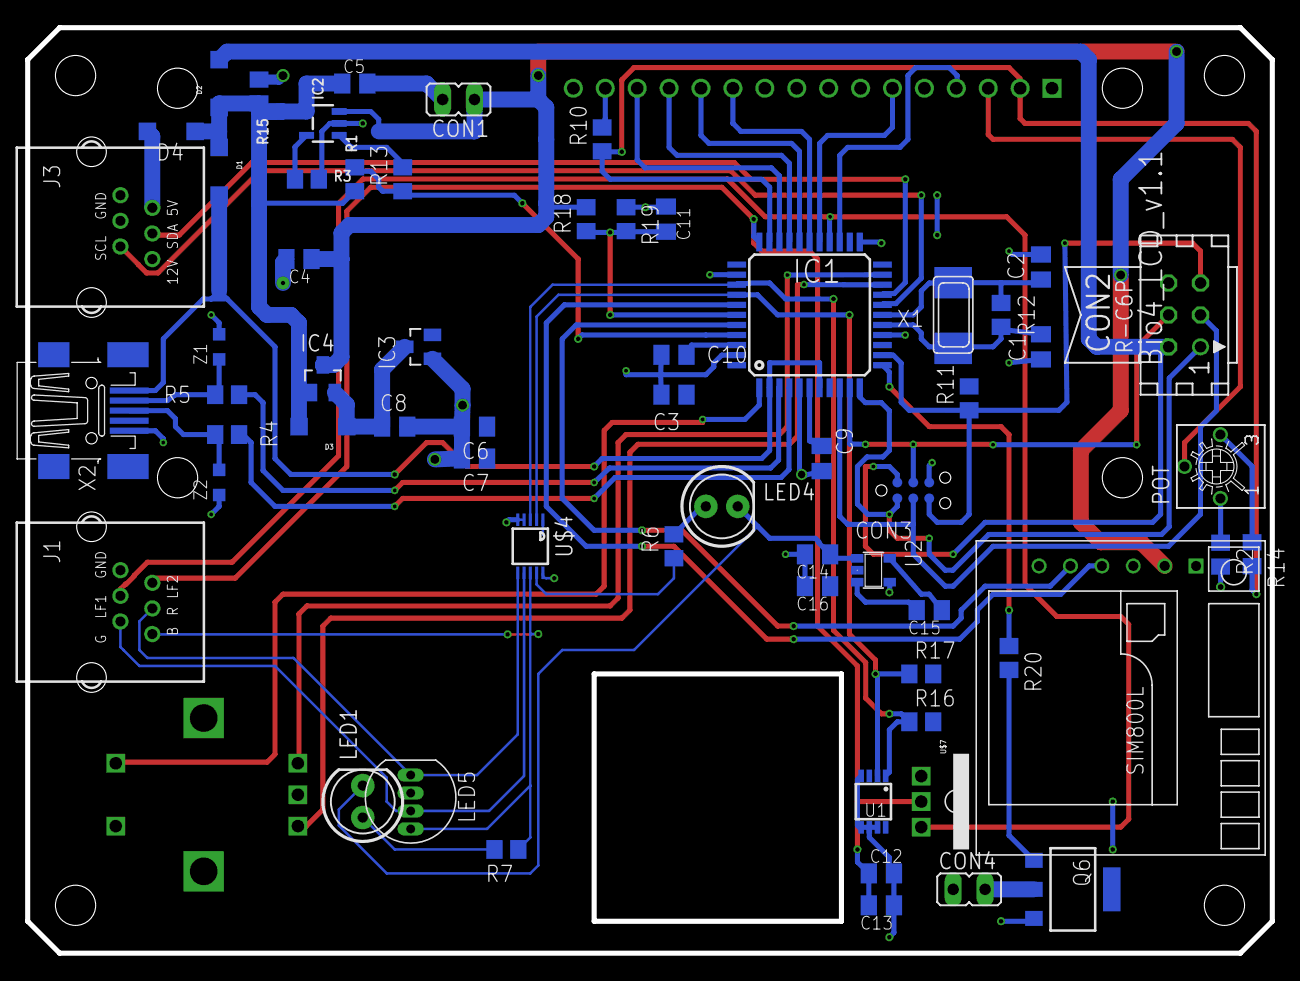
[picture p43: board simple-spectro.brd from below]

Board: 2 copper layers, 99.1 x 73.7 mm, 64 parts (62 on the bottom side), 58 nets.

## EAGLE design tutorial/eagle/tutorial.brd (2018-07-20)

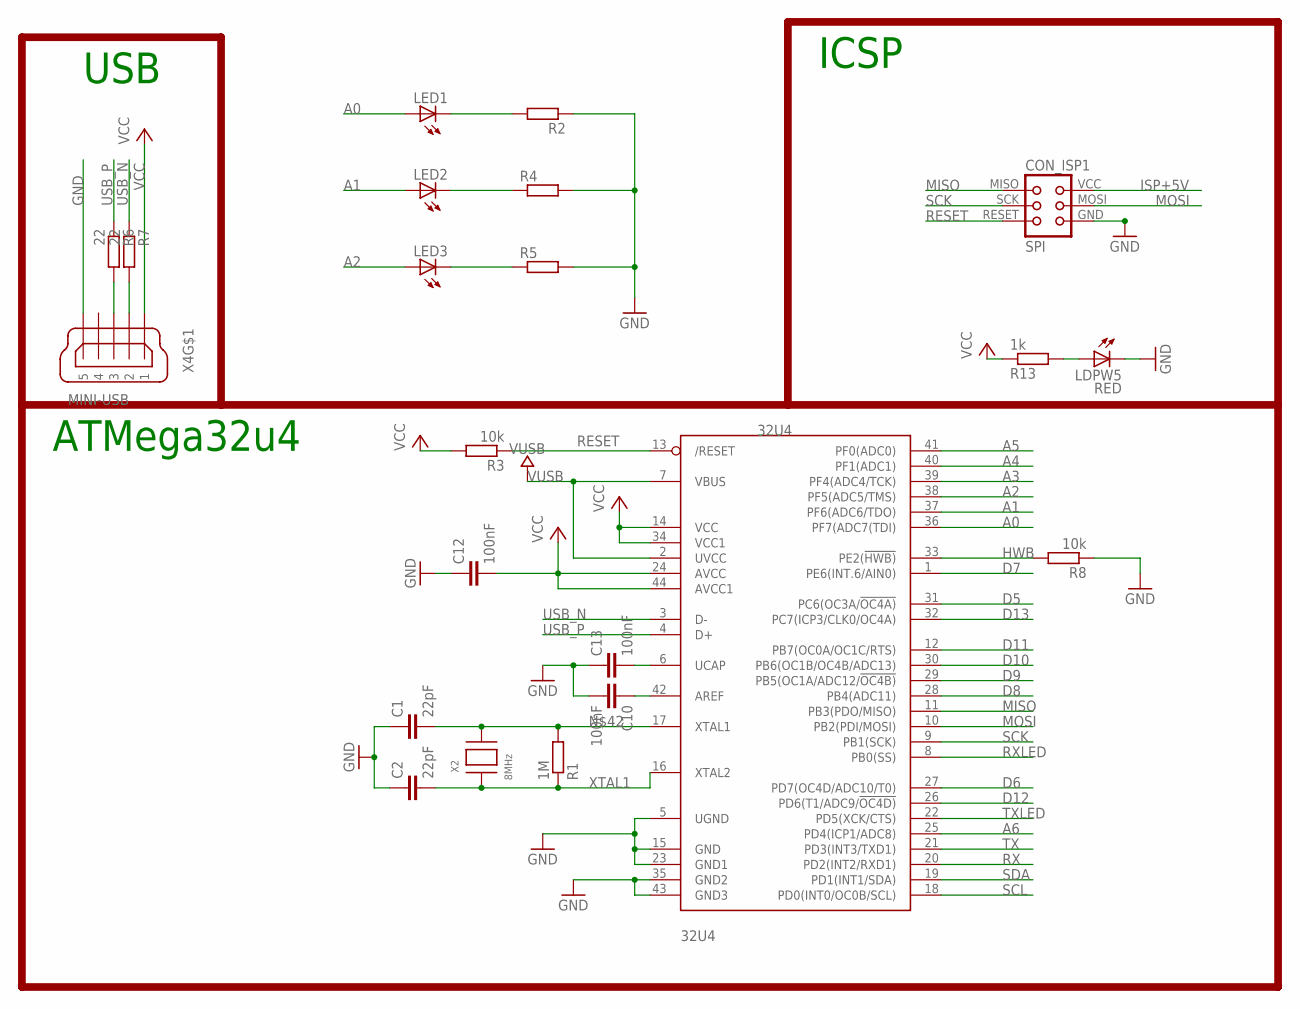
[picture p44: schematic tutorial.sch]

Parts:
32U4: 32U4; TQFP44
C1, C2: 22pF; C1206
C10, C12, C13: 100nF; C1206
CON_ISP1: SPI; TINYISP
LDPW5: RED; LED-1206
LED1, LED2, LED3: LED5MM
R1: 1M; M1206
R2: R-EU_R1206; R1206; LCSC 12345
R3, R8: 10k; M1206
R4, R5: R-EU_R1206; R1206
R6, R7: 22; M1206
R13: 1k; M1206
X2: 8MHz; NX6035
X4: MINI-USB; 32005-201

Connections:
A0: 32U4.36 (PF7(ADC7(TDI)), LED1.A
A1: 32U4.37 (PF6(ADC6/TDO)), LED2.A
A2: 32U4.38 (PF5(ADC5/TMS)), LED3.A
A3: 32U4.39 (PF4(ADC4/TCK))
A4: 32U4.40 (PF1(ADC1))
A5: 32U4.41 (PF0(ADC0))
A6: 32U4.25 (PD4(ICP1/ADC8))
AREF: 32U4.42 (AREF), C10.1
D5: 32U4.31 (PC6(OC3A/!OC4A))
D6: 32U4.27 (PD7(OC4D/ADC10/T0))
D7: 32U4.1 (PE6(INT.6/AIN0))
D8: 32U4.28 (PB4(ADC11))
D9: 32U4.29 (PB5(OC1A/ADC12/!OC4B))
D10: 32U4.30 (PB6(OC1B/OC4B/ADC13))
D11: 32U4.12 (PB7(OC0A/OC1C/RTS))
D12: 32U4.26 (PD6(T1/ADC9/!OC4D))
D13: 32U4.32 (PC7(ICP3/CLK0/OC4A))
GND: 32U4.5 (UGND), 32U4.15 (GND), 32U4.23 (GND1), 32U4.35 (GND2), 32U4.43 (GND3), C1.1, C2.1, C10.2, C12.1, C13.1, CON_ISP1.GND, LDPW5.C, R2.1, R4.2, R5.2, R8.1, X4.5
HWB: 32U4.33 (PE2(!HWB)), R8.2
ISP+5V: CON_ISP1.VCC
MISO: 32U4.11 (PB3(PDO/MISO)), CON_ISP1.MISO
MOSI: 32U4.10 (PB2(PDI/MOSI)), CON_ISP1.MOSI
unnamed: 32U4.6 (UCAP), C13.2
unnamed: LED3.K (C), R5.1
unnamed: LED2.K (C), R4.1
unnamed: LED1.K (C), R2.2
unnamed: LDPW5.A, R13.2
unnamed: 32U4.17 (XTAL1), C1.2, R1.2, X2.P$2
RESET: 32U4.13 (/RESET), CON_ISP1.RESET, R3.1
RX: 32U4.20 (PD2(INT2/RXD1))
RXLED: 32U4.8 (PB0(SS))
SCK: 32U4.9 (PB1(SCK)), CON_ISP1.SCK
SCL: 32U4.18 (PD0(INT0/OC0B/SCL))
SDA: 32U4.19 (PD1(INT1/SDA))
TX: 32U4.21 (PD3(INT3/TXD1))
TXLED: 32U4.22 (PD5(XCK/CTS))
USBC_N: R7.2, X4.2
USBC_P: R6.2, X4.3
USB_N: 32U4.3 (D-), R7.1
USB_P: 32U4.4 (D+), R6.1
VCC: 32U4.14 (VCC), 32U4.24 (AVCC), 32U4.34 (VCC1), 32U4.44 (AVCC1), C12.2, R3.2, R13.1, X4.1
VUSB: 32U4.2 (UVCC), 32U4.7 (VBUS)
XTAL1: 32U4.16 (XTAL2), C2.2, R1.1, X2.P$1

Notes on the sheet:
USB
ICSP
ATMega32u4

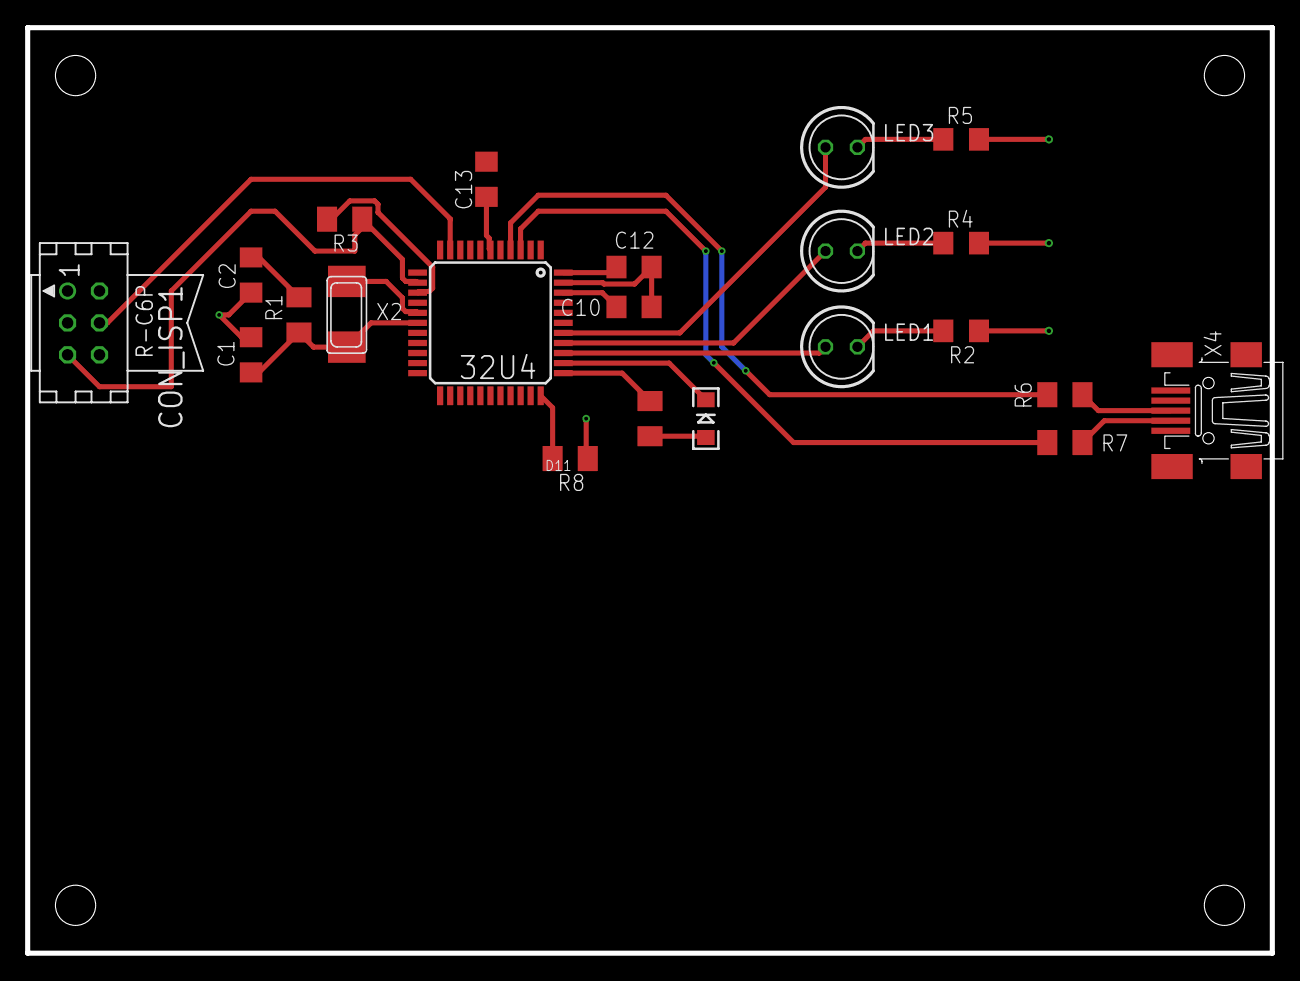
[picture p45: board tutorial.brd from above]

Board: 2 copper layers, 99.1 x 73.7 mm, 22 parts (0 on the bottom side), 23 nets.

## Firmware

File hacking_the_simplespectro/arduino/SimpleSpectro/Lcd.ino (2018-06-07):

#define LANGUAGE 'en'

// https://docs.google.com/spreadsheets/d/1oek6pKHUvD7NI2u9-_iEOfVL-NeUmnj1pZCFRRo7n_4/edit?usp=sharing

#if LANGUAGE == 'en'
#define TEXT_ABSORBANCE "Absorb."
#define TEXT_WAITING_BLANK "Waiting blank"
#define TEXT_WAITING_EXP "Waiting exp."
#define TEXT_ACQUIRING "Acquiring"
#define TEXT_BLANK "Blank"
#define TEXT_SAMPLE "Sample"
#define TEXT_SEQUENCE "Sequence"
#define TEXT_KINETIC "Kinetic"
#define TEXT_STOP "Stop acquis."
#define TEXT_ACQUIRE "Acquire"
#define TEXT_ACQ_SEQUENCE "Acq. sequence"
#define TEXT_CONT_SEQUENCE "Continue seq."
#define TEXT_ACQ_KINETIC "Acq. kinetic"
#define TEXT_CONT_KINETC "Continue kin."
#define TEXT_RESULTS "Results"
#define TEXT_SETTINGS "Settings"
#define TEXT_STATUS "Status"
#define TEXT_UTILITIES "Utilities"
#define TEXT_SLEEP "Sleep"
#define TEXT_TEST_LEDS "Test LED"
#define TEXT_RESET "Reset"
#define TEXT_REBOOT "Reboot"
#define TEXT_MAIN_MENU "Main menu"
#define TEXT_RED "Red"
#define TEXT_GREEN "Green"
#define TEXT_BLUE "Blue"
#define TEXT_UV1 "UV"
#define TEXT_UV2 "UV 2"
#define TEXT_BEFORE_DELAY "Before delay"
#define TEXT_FIRST_DELAY "First delay"
#define TEXT_INTER_DELAY "Inter exp. delay"
#define TEXT_NUMBER_EXP "Number exp."
#define TEXT_RESULT_COLOR "Result color"
#define TEXT_PRESS_NEXT "Press for next"
#endif

#if LANGUAGE == 'es'
#define TEXT_ABSORBANCE "Absorb."
#define TEXT_WAITING_BLANK "Esperando blanco"
#define TEXT_WAITING_EXP "Esperando exp."
#define TEXT_ACQUIRING "Adquiriendo"
#define TEXT_BLANK "Blanco"
#define TEXT_SAMPLE "Muestra"
#define TEXT_KINETIC "Cinetica"
#define TEXT_STOP "Detener"
#define TEXT_ACQUIRE "Adquirir"
#define TEXT_ACQ_KINETIC "Adq. Cinetica"
#define TEXT_RESULTS "Resultados"
#define TEXT_SETTINGS "Ajustes"
#define TEXT_STATUS "Estado"
#define TEXT_UTILITIES "Utilidades"
#define TEXT_SLEEP "Dormir"
#define TEXT_TEST_LEDS "prueba de LED"
#define TEXT_RESET "Reiniciar"
#define TEXT_MAIN_MENU "Menu"
#define TEXT_RED "Rojo"
#define TEXT_GREEN "Verde"
#define TEXT_BLUE "Azul"
#define TEXT_UV1 "UV"
#define TEXT_BEFORE_DELAY "Tiempo inicio"
#define TEXT_FIRST_DELAY "Primera pausa"
#define TEXT_INTER_DELAY "Tiempo entre exp"
#define TEXT_NUMBER_EXP "Numero de exp"
#define TEXT_RESULT_COLOR "Color"
#define TEXT_PRESS_NEXT "Press for next"
#endif



#include <LiquidCrystal.h>

#define LCD_E      6
#define LCD_RS     A6
#define LCD_D4     8
#define LCD_D5     9
#define LCD_D6     10
#define LCD_D7     5
#define LCD_BL     13    // back light
#define LCD_VO     11    // contrast (on / off to spare energy)
#define LCD_ON     MOSI  // power on LCD

#define LCD_NB_ROWS     2
#define LCD_NB_COLUMNS  16


byte lcdPins[] = {LCD_E, LCD_RS, LCD_D4, LCD_D5, LCD_D6, LCD_D7, LCD_VO, LCD_BL, LCD_ON};

LiquidCrystal lcd(LCD_RS, LCD_E, LCD_D4, LCD_D5, LCD_D6, LCD_D7);


#include "lib/RotaryEncoder/Rotary.cpp"

#define ROT_A      0
#define ROT_B      1
#define ROT_PUSH   7

// Rotary encoder is wired with the common to ground and the two
// outputs to pins 2 and 3.
Rotary rotary = Rotary(ROT_A, ROT_B);



boolean rotaryPressed = false;
int rotaryCounter = 0;
boolean captureCounter = false; // use when you need to setup a parameter from the menu



NIL_WORKING_AREA(waThreadLcd, 250);
NIL_THREAD(ThreadLcd, arg) {
  // initialize the library with the numbers of the interface pins
  setupRotary();
  wakeUpScreen();

  setParameter(PARAM_MENU, 0);
  setParameter(PARAM_STATUS, 0);

  while (true) {
    lcdMenu();
    nilThdSleepMilliseconds(40);
  }
}


int noEventCounter = 0;
byte previousMenu = 0;

void lcdMenu() {
  byte currentMenu = getParameter(PARAM_MENU);
  if (previousMenu != currentMenu) { // this is used to clear screen from external process for example
    noEventCounter = 0;
    previousMenu = currentMenu;
  }
  if (rotaryCounter == 0 && ! rotaryPressed) {
    if (noEventCounter < 32760) noEventCounter++;
  } else {
    noEventCounter = 0;
  }
  if (noEventCounter > 250 && getParameter(PARAM_STATUS) == 0) {
    if (currentMenu - currentMenu % 10 != 20) {
      setParameter(PARAM_MENU, 20 + nbLeds);
    }
    captureCounter = false;
  }

#ifdef BATTERY_CHARGING
  if (noEventCounter > 500 && getParameter(PARAM_CHARGING) > 500) { // battery is charging so we are on USB : no sleep !
    noEventCounter = 500;
  }
#endif


  if (noEventCounter > 1500 && getParameter(PARAM_STATUS) == 0) {
    sleepNow();
    noEventCounter = 0;
  }

  boolean doAction = rotaryPressed;
  rotaryPressed = false;
  int counter = rotaryCounter;
  rotaryCounter = 0;
  switch (currentMenu < 100 ? currentMenu - currentMenu % 10 : currentMenu - currentMenu % 50) {
    case 0:
      lcdMenuHome(counter, doAction);
      break;
    case 10:
      lcdMenuSettings(counter, doAction);
      break;
    case 20:
      lcdStatus(counter, doAction);
      break;
    case 30:
      lcdAcquisition(counter, doAction);
      break;
    case 40:
      lcdUtilities(counter, doAction);
      break;
    case 100:
      lcdResults(counter, doAction);
      break;
  }
}

void lcdResults(int counter, boolean doAction) {
  if (doAction) setParameter(PARAM_MENU, 0);
  if (noEventCounter < 2) lcd.clear();

  // calculate the last experiment based on epoch of each experiment
  byte lastExperiment = 1;
  long dataZero = getDataLong(0);
  for (lastExperiment; lastExperiment < maxNbRows; lastExperiment++) {
    if (getDataLong(lastExperiment * dataRowSize) <= dataZero) break;
  }

  updateCurrentMenu(counter, lastExperiment - 1, 50);
  byte start = getParameter(PARAM_MENU) % 50;
  for (byte i = start; i < min(lastExperiment, start + LCD_NB_ROWS); i++) {
    lcd.setCursor(0, i - start);
    lcd.print((getDataLong(i * dataRowSize) - getDataLong(0)) / 1000);
    lcd.print(" ");
    if (getDataLong(getParameter(PARAM_COLOR)) == LONG_MAX_VALUE || getDataLong(i * dataRowSize + getParameter(PARAM_COLOR)) == LONG_MAX_VALUE) {
      lcd.print(F("OVER"));
    } else {
      lcd.print(log10(getDataLong(getParameter(PARAM_COLOR)) / getDataLong(i * dataRowSize + getParameter(PARAM_COLOR))));
    }
    lcd.print(" ");
    lcd.print(getDataLong(i * dataRowSize + getParameter(PARAM_COLOR)));
    lcdPrintBlank(6);
  }
}

void lcdStatus(int counter, boolean doAction) {
  if (doAction) setParameter(PARAM_MENU, 0);
  updateCurrentMenu(counter, nbLeds);
  if (noEventCounter < 2) lcd.clear();
  byte menu = getParameter(PARAM_MENU) % 10;
  if (menu < nbLeds) {
    lcd.setCursor(0, 0);
    printColor(&lcd, CURRENT_PARAMETERS[menu]);
    lcd.setCursor(0, 1);
    lcd.print(F(TEXT_ABSORBANCE));
    lcd.setCursor(8, 1);
    if (getParameter(menu + 5) == INT_MAX_VALUE || getParameter(menu) == INT_MAX_VALUE) {
      lcd.print(F("OVER"));
    } else {
      lcd.print(log10((double)getParameter(menu + 5) / (double)getParameter(menu)));
    }
    lcdPrintBlank(2);
  } else {
    lcd.setCursor(0, 0);
#ifdef TEMPERATURE_ADDRESS
    lcd.print("T:");
    lcd.print(((float)getParameter(PARAM_TEMPERATURE)) / 100, 1);
    lcd.print("\xDF\x43");
#endif
#ifdef BATTERY
    lcd.print(F(" B:"));
    lcd.print(((float)getParameter(PARAM_BATTERY)) / 1000);

#ifdef BATTERY_CHARGING
    if (getParameter(PARAM_CHARGING) > 1000) {
      lcd.print("~");
    } else if (getParameter(PARAM_CHARGING) > 500) {
      lcd.print("+");
    } else {
      lcd.print("-");
    }

#else
    lcd.print("V");
#endif
#endif
    lcd.setCursor(0, 1);
    lcd.print(F("Uptime: "));
    lcd.print(millis() / 1000);
    lcd.print("s");
  }
}

// this code is currently not USED
void lcdDefaultExact(int counter, boolean doAction) {
  if (doAction) setParameter(PARAM_MENU, 0);
  updateCurrentMenu(counter, 1);
  if (noEventCounter < 2) lcd.clear();
  switch (getParameter(PARAM_MENU) % 10) {
    case 0:
      for (byte i = 0; i < min(nbLeds, 4); i++) {
        lcd.setCursor((i % 2) * 8, floor(i / 2));
        printColorOne(&lcd, CURRENT_PARAMETERS[i]);
        lcd.print(": ");
        lcd.print(getParameter(i + 5) - getParameter(i));
        lcdPrintBlank(2);
      }
      break;
    case 1:
      lcd.setCursor(0, 0);
      epochToString(now(), &lcd);
      lcd.setCursor(6, 1);
      lcd.print("s: ");
      lcd.print(millis() / 1000);
      break;
  }
}

void lcdAcquisition(int counter, boolean doAction) {
  byte menu = getParameter(PARAM_MENU) % 10;
  // if it is a sequence we should go to menu only if in an acquisition
  if (counter) { // the button was turned
    setParameter(PARAM_MENU, 0);
  }
  if (doAction) { // the button was pressed
    if (menu == 2 || getParameter(PARAM_STATUS) != STATUS_SEQUENCE) {
      setParameter(PARAM_MENU, 0);
    } else { // next experiment, it is a manual sequence
      setParameter(PARAM_WAIT, 0);
    }
  }
  if (noEventCounter < 2) lcd.clear();
  switch (menu) {
    case 0: // waiting for blank
      lcd.setCursor(0, 0);
      lcd.print(F(TEXT_WAITING_BLANK));
      lcdWait();
      break;
    case 1: // waiting for acquisition
      lcd.setCursor(0, 0);
      lcd.print(F(TEXT_WAITING_EXP));
      lcd.print(getParameter(PARAM_NEXT_EXP));
      lcdWait();
      break;
    case 2: // acquiring
      lcd.setCursor(0, 0);
      lcd.print(F(TEXT_ACQUIRING));
      lcd.setCursor(0, 1);
      if (getParameter(PARAM_NEXT_EXP) == 0) {
        lcd.print(F(TEXT_BLANK));
      } else if (getParameter(PARAM_NEXT_EXP) == 1) {
        lcd.print(F(TEXT_SAMPLE));
      } else if (getParameter(PARAM_NEXT_EXP) > 1) {
        if ( getParameter(PARAM_STATUS) == STATUS_SEQUENCE) {
          lcd.print(F(TEXT_KINETIC));
        } else {
          lcd.print(F(TEXT_SEQUENCE));
        }
        lcdPrintBlank(1);
        lcd.print(getParameter(PARAM_NEXT_EXP));
      }
      break;
    case 3: // TEST mode
      lcd.setCursor(0, 0);
      lcd.print("R:");
      lcd.print(getDataLong(1));
      lcdPrintBlank(6);
      lcd.setCursor(8, 0);
      lcd.print("G:");
      lcd.print(getDataLong(2));
      lcdPrintBlank(6);
      lcd.setCursor(0, 1);
      lcd.print("B:");
      lcd.print(getDataLong(3));
      lcdPrintBlank(6);
      lcd.setCursor(8, 2);
      lcd.print("U:");
      lcd.print(getDataLong(4));
      lcdPrintBlank(6);
  }
}

void lcdWait() {
  lcd.setCursor(0, 1);
  if ( getParameter(PARAM_STATUS) == STATUS_SEQUENCE) { // need to press enter for next acquisition
    lcd.print(F(TEXT_PRESS_NEXT));
  } else {
    lcd.print(getParameter(PARAM_WAIT));
    lcd.print(" s ");
  }
}


void lcdNumberLine(byte line) {
  lcd.print(getParameter(PARAM_MENU) % 10 + line + 1);
  if (line == 0) {
    lcd.print(".*");
  } else {
    lcd.print(". ");
  }
}

void updateCurrentMenu(int counter, byte maxValue) {
  updateCurrentMenu(counter, maxValue, 10);
}

void updateCurrentMenu(int counter, byte maxValue, byte modulo) {
  byte currentMenu = getParameter(PARAM_MENU);
  if (captureCounter) return;
  if (counter < 0) {
    setParameter(PARAM_MENU, currentMenu + max(counter, - currentMenu % modulo));
  } else if (counter > 0) {
    setParameter(PARAM_MENU, currentMenu + min(counter, maxValue - currentMenu % modulo));
  }
}
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

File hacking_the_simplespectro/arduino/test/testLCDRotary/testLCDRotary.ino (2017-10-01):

#include <LiquidCrystal.h>

#define LCD_E      6
#define LCD_RS     A6
#define LCD_D4     8
#define LCD_D5     9
#define LCD_D6     10
#define LCD_D7     5
#define LCD_BL     13    // back light
#define LCD_VO     11    // contrast (on / off to spare energy)
#define LCD_ON     MOSI  // power on LCD

byte pins[] = {LCD_E, LCD_RS, LCD_D4, LCD_D5, LCD_D6, LCD_D7, LCD_VO};

#define LCD_NB_ROWS     2
#define LCD_NB_COLUMNS  16

// initialize the library with the numbers of the interface pins
LiquidCrystal lcd(LCD_RS, LCD_E, LCD_D4, LCD_D5, LCD_D6, LCD_D7);

#define PARAM_A           0
#define PARAM_B           1
#define PARAM_C           2
#define PARAM_D           3
#define PARAM_E           4
#define PARAM_F           5


boolean rotaryPressed = false;
int rotaryCounter = 0;
int currentMenu = 0;
boolean captureCounter = false; // use when you need to setup a parameter from the menu
long lastRotaryEvent = millis();

void setup() {
  Serial.begin(115200);

  setupRotary();
  pinMode(LCD_BL, OUTPUT);
  digitalWrite(LCD_BL, HIGH); // backlight
  pinMode(LCD_ON, HIGH); // LCD on / off
  digitalWrite(LCD_ON, HIGH); // LCD on
  lcd.begin(LCD_NB_COLUMNS, LCD_NB_ROWS);

}

void loop() {
  lcdMenu();
  delay(40);
}

byte noEventCounter = 0;
void lcdMenu() {
  if (rotaryCounter == 0 && ! rotaryPressed) {
    if (noEventCounter < 255) noEventCounter++;
  } else {
    noEventCounter = 0;
  }
  if (noEventCounter > 250) {
    currentMenu = 20;
    captureCounter = false;
    noEventCounter = 0;
  }
  boolean doAction = rotaryPressed;
  rotaryPressed = false;
  int counter = rotaryCounter;
  rotaryCounter = 0;


  switch (currentMenu - currentMenu % 10) {
    case 0:
      lcdMenuHome(counter, doAction);
      break;
    case 10:
      lcdMenuSettings(counter, doAction);
      break;
    case 20:
      lcdDefault(counter, doAction);
      break;
  }
}

void lcdDefault(int counter, boolean doAction) {
  if (doAction) currentMenu = 0;
  updateCurrentMenu(counter, 1);
  if (noEventCounter < 2) lcd.clear();
  switch (currentMenu % 10) {
    case 0:
      lcd.setCursor(0, 0);
      lcd.print("A:");
      lcd.print(getParameter(PARAM_A));
      lcdPrintBlank(2);
      lcd.setCursor(8, 0);
      lcd.print("B:");
      lcd.print(getParameter(PARAM_B));
      lcdPrintBlank(2);
      lcd.setCursor(0, 1);
      lcd.print("C:");
      lcd.print(getParameter(PARAM_C));
      lcdPrintBlank(2);
      lcd.setCursor(8, 1);
      lcd.print("D:");
      lcd.print(getParameter(PARAM_D));
      lcdPrintBlank(2);
      break;
    case 1:
      lcd.setCursor(8, 1);
      lcd.print("s:");
      lcd.print(millis() / 1000);
      break;
  }

}


void lcdNumberLine(byte line) {
  lcd.print(currentMenu % 10 + line + 1);
  if (line == 0) {
    lcd.print(".*");
  } else {
    lcd.print(". ");
  }
}

void updateCurrentMenu(int counter, byte maxValue) {
  if (captureCounter) return;
  if (counter < 0) {
    currentMenu += max(counter, - currentMenu % 10);
  } else if (counter > 0) {
    currentMenu += min(counter, maxValue - currentMenu % 10);
  }
}
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

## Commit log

2017-07-08 First version
    [simple-spectro.brd, simple-spectro.sch]
2017-07-08 Working on v1.0.1
    [simple-spectro.brd, simple-spectro.sch]
2017-07-09 v1.1.0 nearly final design
    [simple-spectro.brd, simple-spectro.sch]
2017-07-09 v1.1.0 submitted for PCB
    [simple-spectro.GBL, simple-spectro.GBO, simple-spectro.GBS, simple-spectro.GTL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]
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2017-07-15 all components to 0805
    [simple-spectro.brd, simple-spectro.sch]
2017-07-21 STL Files
    [spectro_boitier.stl, spectro_couvercle.stl]
2017-07-22 add -3.3v
    [simple-spectro.brd, simple-spectro.sch]
2017-07-22 New versions
    [spectro_boitier.stl, spectro_boitier_v2.stl, spectro_couvercle.stl, spectro_couvercle_v2.stl]
2017-07-22 Thinner holes in columns + CAD files
    [boitier.FCStd, simplespectro_v2.FCStd, spectro_couvercle_v2.stl]
2017-07-22 add button deboucing and PARAM_MENU
    [simple-spectro.brd, simple-spectro.sch]
2017-07-24 Fixed all issues
    [boitier.FCStd, boitier_v2.FCStd, boitier_v2.stl, simplespectro_v2.FCStd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]
2017-07-24 Final changes
    [boitier_v2.FCStd]
2017-07-24 Final stl versions
    [boitier_v2.stl, simplespectro_v3.FCStd, simplespectro_v3.stl]
2017-07-24 Change in files locations
    [boitier_v2.stl, simplespectro_v3.stl]
2017-07-26 Issues should all be fixed
    [boitier_v2.FCStd, boitier_v2.stl, simplespectro_v3.FCStd, simplespectro_v3.stl]
2017-07-27 Fixed slots
    [simplespectro_v3.FCStd, simplespectro_v3.stl]
2017-07-28 Holes + moved usb port
    [boitier_v2.FCStd, boitier_v2.stl]
2017-07-28 Deeper holes + USB port checked
    [boitier_v2.FCStd, boitier_v2.stl]
2017-07-28 New parameters
    [boitier_v2.FCStd]
2017-08-01 Fixed issues
    [simplespectro_v3.FCStd, simplespectro_v3.stl]
2017-08-01 Added battery walls on the case
    [boitier_v2.FCStd, boitier_v2.stl]
2017-08-01 Corrected battery walls
    [boitier_v2.FCStd, boitier_v2.stl]
2017-08-10 Shorter sample holder
    [simplespectro_v3.FCStd, simplespectro_v3.stl]
2017-08-15 clear data for kinetic and add absorbance
    [simple-spectro.brd]
2017-08-18 fixed new issues
    [simplespectro_v3.FCStd, simplespectro_v3.stl]
2017-08-18 changed "chanfrein" types
    [simplespectro_v3.FCStd, simplespectro_v3.stl]
2017-08-20 remove most of the pcf to increase cad speed
    [simplespectro_v3.FCStd]
2017-08-21 simplification of the box
    [simplespectro_v3.FCStd]
2017-08-22 work in progress on the top design
    [top.fcstd]
2017-08-22 fix usb hole
    [top.fcstd]
2017-08-22 first version of new top
    [top.fcstd, top.stl]
2017-08-22 add missing chamfer and correct rotary hole
    [top.fcstd]
2017-08-22 add stl
    [top.stl]
2017-09-08 add pcb-descriptions
    [simple-spectro.dxf]
2017-09-12 increase hole of rotary
    [top.fcstd, top.stl]
2017-09-14 update to simplify
    [simple-spectro.GBL, simple-spectro.GBO, simple-spectro.GBS, simple-spectro.GTL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]
2017-09-14 work to move components to 1206
    [simple-spectro.brd, simple-spectro.sch]
2017-09-14 final version of eagle v1.2.0
    [simple-spectro.GBL, simple-spectro.GBO, simple-spectro.GBS, simple-spectro.GTL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]
2017-09-14 correct version v1.2.0
    [simple-spectro.brd]
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2017-09-30 remove useless file and update top
    [simplespectro_v3.FCStd, simplespectro_v3.stl, top.fcstd, top.stl]
2017-09-30 working on full box
    [boitier_v2.FCStd, boitier_v2.stl, top.fcstd]
2017-09-30 box containing top and bottom
    [box.fcstd, top.fcstd]
2017-10-01 add bottom stl
    [bottom.stl, box.fcstd]
2017-10-01 correct bottom
    [bottom.stl]
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2017-10-01 work in progress select custom leds
    [box.fcstd]
2017-10-01 correct battery case size
    [bottom.stl, box.fcstd]
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2017-10-01 update program to deal better with results
    [box.fcstd, top.stl]
2017-10-01 add missing feet in top0
    [top.stl]
2017-10-01 trying to improve rotary button and cad
    [box.fcstd]
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2017-10-08 improve look of schema
    [simple-spectro.sch]
2017-10-09 work in progress 2d freecad
    [2d-box.fcstd]
2017-10-09 working b ox
    [2d-box.fcstd]
2017-10-14 Add eagle example
    [simple-spectro.brd, simple-spectro.sch]
2017-10-14 rename files
    [tutorial.brd, tutorial.sch]
2017-10-15 test openscad
    [openscad.scad]
2017-10-15 work inp rogress on front and openSCAD
    [openscad.scad]
2017-10-16 work in progress with openSCAD
    [openscad.scad]
2017-10-16 work in progress on box
    [openscad.scad]
2017-10-17 work in progress
    [openscad.scad, test.stl]
2017-10-17 new test
    [openscad.scad, test.stl]
2017-10-18 update pcb values
    [simple-spectro.brd, simple-spectro.sch]
2017-10-18 add manufacturer references for BOM
    [box.fcstd, openscad.scad, simple-spectro.brd, simple-spectro.sch]
2017-10-19 towards final alu design
    [bottom.stl, full.stl, openscad.scad]
2017-10-19 add files for new price offer with assembly
    [simple-spectro.GBL, simple-spectro.GBO, simple-spectro.GBS, simple-spectro.GTL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]
2017-10-19 add logo on alu design
    [openscad.scad]
2017-10-19 correct pdb space to 1
    [bottom.stl, logo.dxf, openscad.scad]
2017-10-20 remove right angles
    [simple-spectro.brd]
2017-10-21 towards final box
    [bottom.stl, full.stl, openscad.scad, simple-spectro.GBL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]
2017-10-21 add alu top
    [full.stl, top.stl]
2017-10-22 remove hull from cuvette
    [openscad.scad]
2017-10-22 add freecad model based on openscad
    [model.fcstd]
2017-10-26 update box
    [bottom.stl, full.stl, openscad.scad, simple-spectro.brd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]
2017-10-28 fix box size
    [2d-box.fcstd]
2017-10-28 update bom
    [simple-spectro.brd, simple-spectro.sch]
2017-10-28 add eagle export files
    [simple-spectro.csv]
2017-10-28 add i2c temperature sensor
    [simple-spectro.brd, simple-spectro.sch]
2017-10-28 add battery monitoring
    [simple-spectro.brd, simple-spectro.sch]
2017-10-28 clean up
    [simple-spectro.brd, simple-spectro.sch]
2017-10-28 working on vibration
    [simple-spectro.brd, simple-spectro.sch]
2017-10-29 final design for price quote 1206 elecrow
    [simple-spectro.GBL, simple-spectro.GBO, simple-spectro.GBS, simple-spectro.GTL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]
2017-11-01 work on 0805
    [simple-spectro.brd, simple-spectro.csv, simple-spectro.sch]
2017-11-02 pcb v1.4 elecrow
    [simple-spectro.GBL, simple-spectro.GBO, simple-spectro.GBS, simple-spectro.GTL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]
2017-11-12 update value
    [simple-spectro.brd, simple-spectro.csv, simple-spectro.sch]
2017-11-25 move the pot to prevent contact with battery
    [simple-spectro.brd]
2017-11-25 remove hull and deeper hole for battery
    [openscad.scad]
2017-11-27 update box to scratch the battery
    [bottom.stl, full.stl, simple-spectro.brd, top.stl]
2017-11-27 change resolution
    [openscad.scad]
2017-12-02 add old alu box
    [bottom16-no.stl, openscad.scad, top16-no.stl]
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2017-12-03 add temperature and battery sensor for model B
    [simple-spectro.brd, simple-spectro.sch]
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2018-01-13 fix (PCB): change resistor for backlight to 0 ohm
    close #37
    [simple-spectro.brd, simple-spectro.sch]
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2018-02-08 fix screen size
    [screen.dxf, screen.scad]
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2018-03-08 fix eagle demo and 22 ohms position
    [tutorial.brd]
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2018-03-21 fix tutorial not to check layer 2 and 15
    [tutorial.brd]
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2018-04-18 fix small box
    [100x50x30.dxf, 50x50x30.dxf, 50x50x40.dxf, 60x60x30.dxf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]
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2018-06-04 fix rotary push button mistake
    [simple-spectro.brd, simple-spectro.sch]
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2018-06-07 fix https://github.com/Hackuarium/simple-spectro/issues/56
    [simple-spectro.brd, simple-spectro.sch]
2018-06-07 fix https://github.com/Hackuarium/simple-spectro/issues/59
    [simple-spectro.brd, simple-spectro.sch]
2018-06-07 fix https://github.com/Hackuarium/simple-spectro/issues/55
    [simple-spectro.brd, simple-spectro.sch]
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2018-06-10 fix rotary push in pcb
    [simple-spectro.brd, simple-spectro.sch]
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2018-07-12 fix little extra edge in cuvette
    [top.scad]
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2018-10-17 first correction
    [simple-spectro.brd, simple-spectro.sch]
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2018-10-21 update version and fix width
    [simple-spectro.brd, simple-spectro.sch]
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2019-01-28 fix denomination of i2c D/A
    [simple-spectro.sch]
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2019-03-08 fix inside hole for rotary button place
    [top.scad]
2019-03-08 fix rotary push button hole position
    [openscad.scad]
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2019-03-09 Fix semicolumn
    [bottom.scad]
2019-03-09 Fix bottom step
    [bottom.step]
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2020-02-15 fix: laser cut box
    [spectro-color.dxf, spectro_center_3_15_gap01.dxf]
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2024-07-23 3dp cell holder
    This parts replaces the four small laser cut inner parts.
    [spectro_cell_holder_3dp.3mf, spectro_cell_holder_3dp.SLDPRT, spectro_cell_holder_3dp.STEP]
2024-07-25 fix: 3dp cell holder new version
    [spectro_cell_holder_3dp.3mf, spectro_cell_holder_3dp.SLDPRT, spectro_cell_holder_3dp.STEP]
2024-07-25 fix: add bottom to cell holder and ajust cell fit
    [spectro_cell_holder_3dp.3mf, spectro_cell_holder_3dp.SLDPRT, spectro_cell_holder_3dp.STEP]
2024-07-28 fix: change bottom wall side
    Change the position of the bottom wall relative to the diagonal wall height to ensure cell fit when assembled.
    [spectro_cell_holder_3dp.3mf, spectro_cell_holder_3dp.SLDPRT, spectro_cell_holder_3dp.STEP]

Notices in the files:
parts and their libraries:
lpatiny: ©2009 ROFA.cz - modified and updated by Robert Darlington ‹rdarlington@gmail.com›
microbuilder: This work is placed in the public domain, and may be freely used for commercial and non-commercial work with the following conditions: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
